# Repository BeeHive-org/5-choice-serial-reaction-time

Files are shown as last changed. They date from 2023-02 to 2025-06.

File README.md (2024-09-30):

# Serial Reaction Chamber

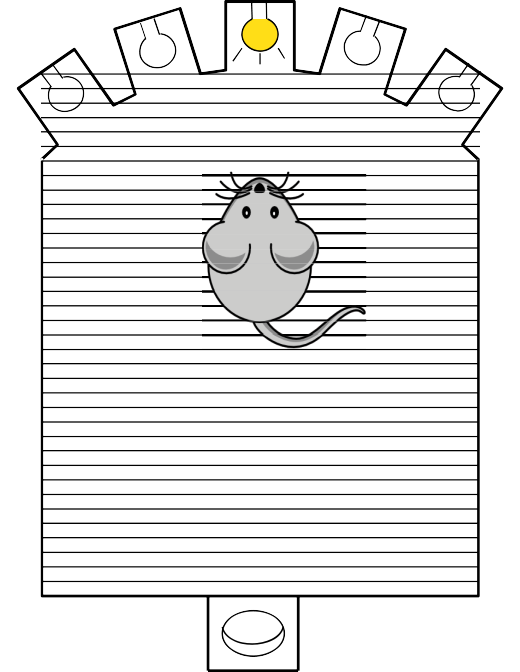
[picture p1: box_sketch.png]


The chamber can be used to observe small rodents response to light stimulus. 

It has holes with a light on one end and a feeding slot with a light in the opposite end. Depending on the behavoiur being experimented the animal needs to poke it's nose into the correct hole and feeding occurs in accordance to the experiemntal rules.

 Its an implementation of a complete behavioural box using BeeHive, off the shelf components and 3D printed parts.
  
---

### Hardware:
- The supporting hardware for the project:
     * food_dispencer
    * reaction_chamber 
- Running on the Beehive platform under:
     + Electronics 

### Software:
-    The beehive platform uses ESP32 which can run either micropython or C++. 
-     testcode is provided in microPython.
 -   You can also use Bonsai for data collection on PC however this implimentation is not covered under this documentation.

If you wish to build the complete box please look at the [Overal BOM]{BOM} otherwise you can find indvidual sectional Bill of materials under each tab.

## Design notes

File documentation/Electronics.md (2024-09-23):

# Electronics

The electronics combine the Esp32 and Bee hive central hub:

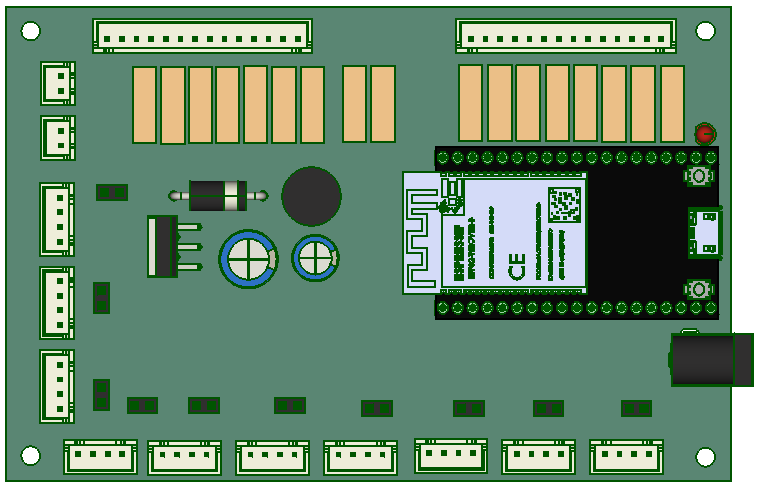
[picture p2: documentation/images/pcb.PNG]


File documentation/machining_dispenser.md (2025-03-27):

[3d printer]:Parts.yaml#3dprinter
[Laser cutter]:Parts.yaml#Lasercutter
[PLA filament]:Parts.yaml#PLAfilament
[clear plastic sheet]:Parts.yaml#ClearSheet

# Machining Guide

>! To accomplish this section you should have appropriate machining skills. 
>? You can outsource the parts by sending this section to your preffered machining techinician or company.

{{BOM}}

##Printing parts{pagestep}

>? Support from bed plate is required. It is unnecesary to add support everywhere. Add a brim to ensure the small parts are anchored appropriately. 

*  Use a [3d printer]{qty: 1, cat:machine} and [PLA filament]{ qty:100g, cat:material} to print the following parts:
       +  [Motor holder](models/Motor_holder.stl)
       +  [Tank base](models/Allparts.stl)
       +  [Chute](models/chute_with_mount.stl)
       +  [Feed tank](models/Feed_tank.stl)
       +  [Rotor](models/Rotor.stl)

## Laser cut parts {pagestep}

* Use a [Laser cutter]{qty: 1, cat:machine} and [clear plastic sheet]{qty:1, cat: material} to produce the following:
    + [Outer cover](models/Outer_cover.svg)
    + [Inner cover](models/Inner_cover.svg)

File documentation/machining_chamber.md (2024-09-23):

[3d printer]:Parts.yaml#3dprinter
[Laser cutter]:Parts.yaml#Lasercutter
[PLA filament]:Parts.yaml#PLAfilament
[clear plastic sheet]:Parts.yaml#ClearSheet
[maker beam XL]:Parts.yaml#MakerBeamXL
[150mm mini hacksaw]:Parts.yaml#Hacksaw
[M3 tap set]:Parts.yaml#M3tapset
[tap wrench]:Parts.yaml#Tapwrench

# Machining Guide

>! To accomplish this section you should have appropriate machining skills. 
>? You can outsource the parts by sending this section to your preffered machining techinician or company.

{{BOM}}

## Printing parts{pagestep}

>? Support from bed plate is required. It's unnecesary to add support everywhere. Add a brim to ensure the small parts are anchored appropriately. 

*  Use a [3d printer]{qty: 1, cat:machine} and [PLA filament]{ qty:500g, cat:material} to print the following parts:
    + [Latch handle](models/Latch_handle.stl)
    + [Latch base](models/Latch_base.stl)
    + [Electronics top](models/Electronics_top.stl)
    + [Corner](models/corner.stl)
    + [Feeding wall](models/Feeding_wall.stl)
    + [Led series wall](models/Led_series_wall.stl)
    + [Curved wall](models/Curved_wall.stl)
    + [Tunnel connector](models/Tunnel_connector.stl)
    + [Tunnel clamp](models/Tunnel_clamp.stl)
    +  [Hinge](models/Hinge.stl)
    + [Trap latch](models/Trap_latch.stl)
    + [Groove pins](models/Grooved_pin.stl)

## Laser cut parts{pagestep}
* Use a [Laser cutter]{qty: 1, cat:machine} and [clear plastic sheet]{qty:1, cat: material} to produce the following:
     + 1 pc of [Ecase_Back](models/Ecase_Back.svg)
     + 1 pc of [Ecase_Base](models/Ecase_Base.svg)
     + 1 pc of [Ecase_Front](models/Ecase_Front.svg)
     +  2 pcs of [Ecase_R&L](models/Ecase_RnL.svg)
     + 1 pc of [platform support](models/Platform_support.svg)
     + 2 pcs of [Platform base](models/Platform_base.svg)
     + 1 pc of [side entry wall](models/Side_entry_wall.svg)
     + 1 pc of [side plain wall](models/Side_plain_wall.svg)
     + 1 pc of [case back](models/Excrete_panel_RnL.svg),
     + 1 pc of [case base](models/Excrete_panel_base.svg)
     + 1 pc of [case front](models/Excrete_panel_RnL.svg) 
     + 1 pc of [case right](models/Excrete_panel_FnB.svg) 
     + 1 pc of [case left](models/Excrete_panel_FnB.svg) 

## Cut and thread beams{pagestep}
 + Using [150mm mini hacksaw]{Qty:1,cat: Tool} cut 2 pcs 200mm long and 6 pcs 150mm long from the [maker beam XL]{Qty:1,cat: material}
 
  + From the [M3 tap set]{Qty:1,cat: Tool} place the taping screw on the [tap wrench]{Qty:1,cat: Tool} then make threads on the holes at the end of the maker beam xl pieces.

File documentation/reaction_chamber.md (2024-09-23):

# Reaction chamber

The chamber is used to track mice reaction time using light as a training cue. Coupled with a camera it can be used to collect data on movement patterns, posture and other behaviours. 

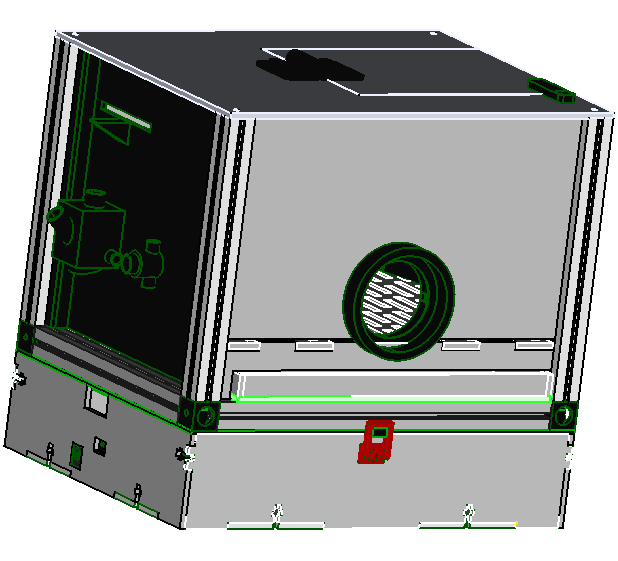
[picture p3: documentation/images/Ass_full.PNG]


Before you start ensure you have everything by checking the [bill of materials page]{BOM}.

You can then follow the guides below:

* [.](machining_chamber.md){step}
* [.](make_chamber.md){step}

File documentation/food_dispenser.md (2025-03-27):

# Food dispenser

An automated feeding and storage tank for small animals during lab test. In this project its being used to reward the animal under test. After testing is done the feeding tank should be filled and programed to auto feed mode to ensure the animal is feed as per the diatery requirements.

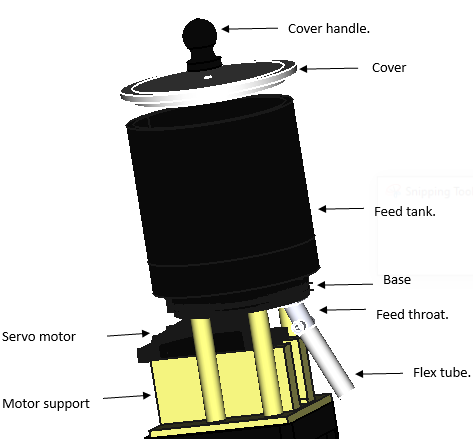
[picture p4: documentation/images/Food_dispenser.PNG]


Before you start ensure you have everything by checking the [bill of materials page]{BOM}.

You can then follow the guides below:

* [.](machining_dispenser.md){step}
* [.](make_dispenser.md){step}

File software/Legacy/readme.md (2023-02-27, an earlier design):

this folder contains the code to run the 5-CSRTT training and test.  
    
To setup the board to communicate over wifi and use Belay users need to:  
- Make a copy of the "passes_template.py" and rename it to passes.py  
- Change the newly created "passes.py" file to contain needed information about the network and where the IP address for Bonsai  
- Save "passes.py" on the ESP32 board  
- Save "webrepl_cfg.py" on the ESP32 board  
-  

More documentation on Belay connections here:  
https://belay.readthedocs.io/en/latest/Connections.html  

---  

phases of training and testing are:  
 -food_magazine  
 -phase1  
 -phase2  
 -stage_5csrtt_task  
 -stage_9_task  
 -stage_10_task  
 -stage_11_task  
 -stage_12_task

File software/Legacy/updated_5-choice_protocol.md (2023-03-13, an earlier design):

##### Updated 5-Choice Training Program

## New nosepoke light to trigger trial start at the back panel in the middle
## Magazine will be moved to right hand side

* TSL = Trial Start Light
* TSS = Trial Start Sensor
* MS = Magazine Sensor
* FD = food delivery

## Magazine Training:

* TSL turns on + food is delivered
* mouse nosepokes into the magazine to get the food
* this triggers TSL to turn off + variable ITI begins (4,8,16,or 32 sec)
* next trial begins
* This phase is 50 trials.

## Training 1 (Phase 1):

* TSL turns on 
* mouse nosepokes into Trial Start Hole + TSS detects it
* TSL turns off + food is delivered
* mouse nosepokes into the magazine to get the food
* next trial begins
* This phase is 50 trials.

## Training 2 (Phase 2):

* TSL turns on 
* mouse nosepokes into Trial Start Hole + TSS detects it
* TSL turns off
* 5 stimulus lights on the opposite wall turns on
* mouse nosepokes into one of them (sensor detects it)
* 5 stimulus lights turn off
* food is delivered
* next trial begins
* This phase is 50 trials.

## Training 3 (Phase 3):

* TSL turns on 
* mouse nosepokes into Trial Start Hole + TSS detects it
* TSL turns off
* 5 sec ITI
* Randomly chosen 1 stimulus light on the opposite wall turns on
* mouse nosepokes into one of them (sensor detects it)
* If nosepoked into a non-illumniated hole, there is no consequence, the trial begins again.
  * all lights off, no time out, start at the beg. again.
* If mouse nosepokes into the illuminated light, stimulus light turns off.
* food is delivered
* once mouse collects the food, there is 20 sec consumption interval (no light is on)
* next trial begins
* This phase is 100 trials.

## 5-Choice Training (Phase 4-8):

* TSL turns on 
* mouse nosepokes into Trial Start Hole + TSS detects it
* TSL turns off
* 5 sec ITI
* one Nosepoke turns on for SD time and turns off after that duration.
* If nosepoke into stimulus lights during ITI, record it as premature and Time-Out for 5 sec (no lights).
* Randomly chosen 1 stimulus light on the opposite wall turns on
* mouse nosepokes into one of them (sensor detects it)
* If nosepoked into a non-illumniated hole, record it as incorrect and Time-Out for 5 sec (no lights).
* If mouse nosepokes into the illuminated light, stimulus light turns off.
* food is delivered
* once mouse collects the food from magazine, there is 20 sec consumption interval (no light is on)
* If no nosepokes (SD+4sec), record it as an omission and Time-Out for 5 sec (no lights).
* next trial begins
* This phase is 100 trials.

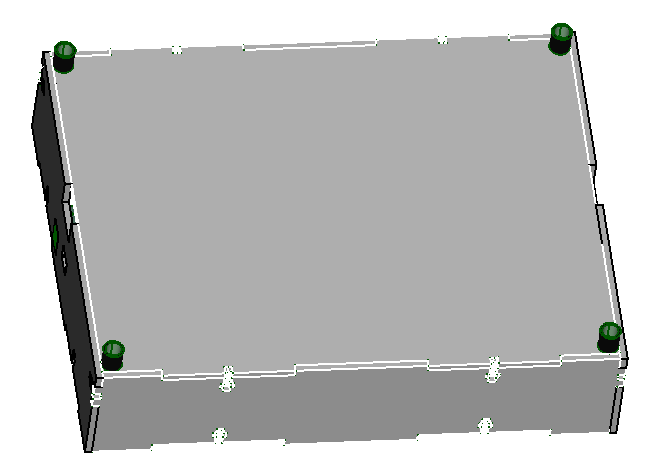
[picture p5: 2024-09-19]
documentation/images/Electronics_full.PNG

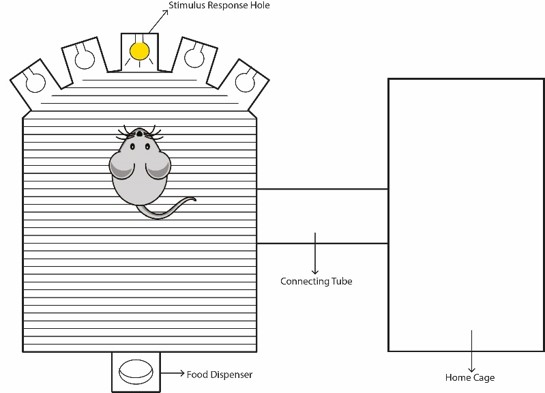
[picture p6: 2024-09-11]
documentation/images/CombiCage_sketch.jpg

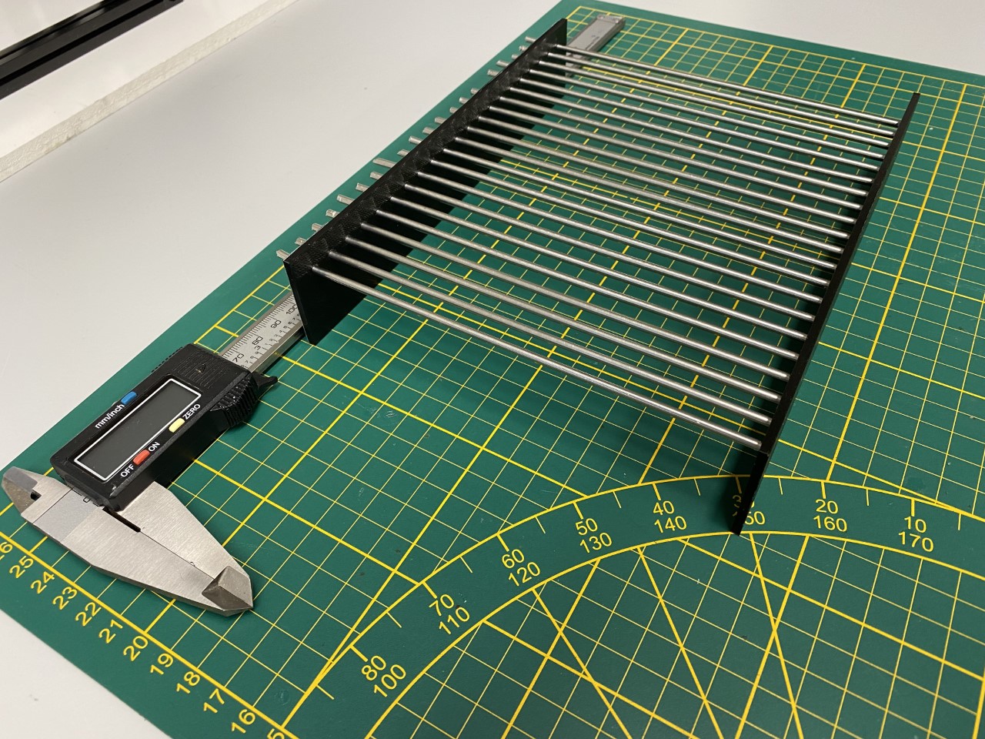
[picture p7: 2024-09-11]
documentation/images/grid_5.jpg

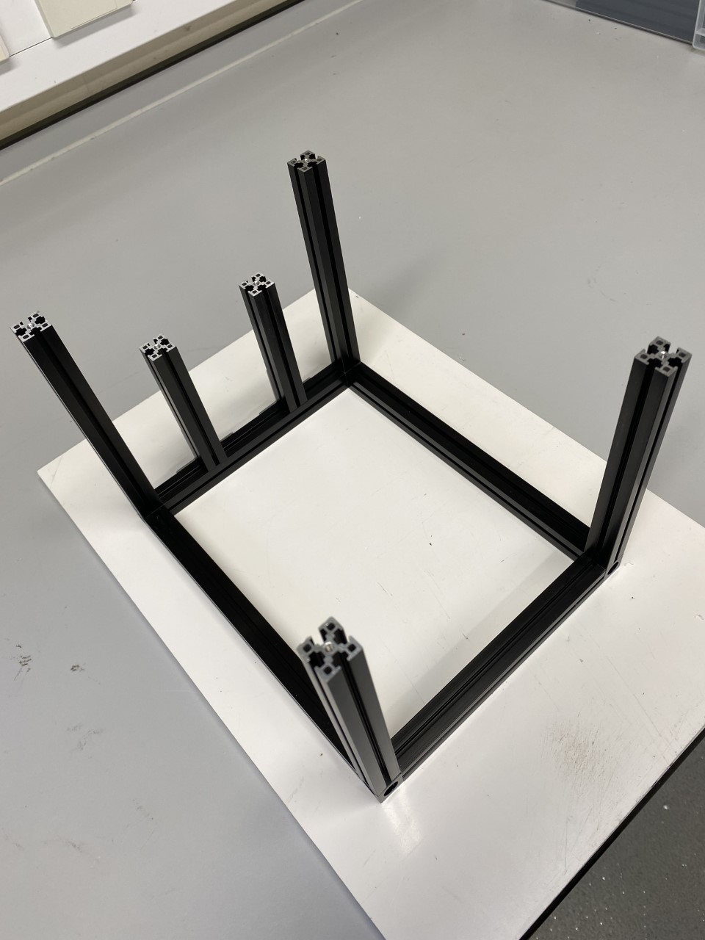
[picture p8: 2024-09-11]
documentation/images/frame_2.jpg

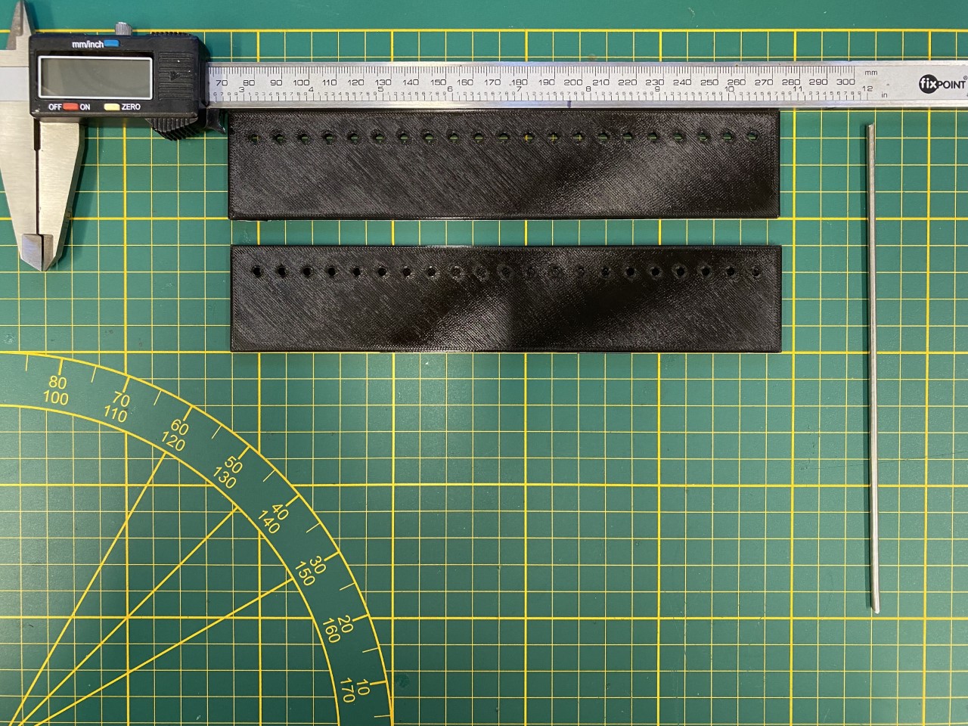
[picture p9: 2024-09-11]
documentation/images/grid_2.jpg

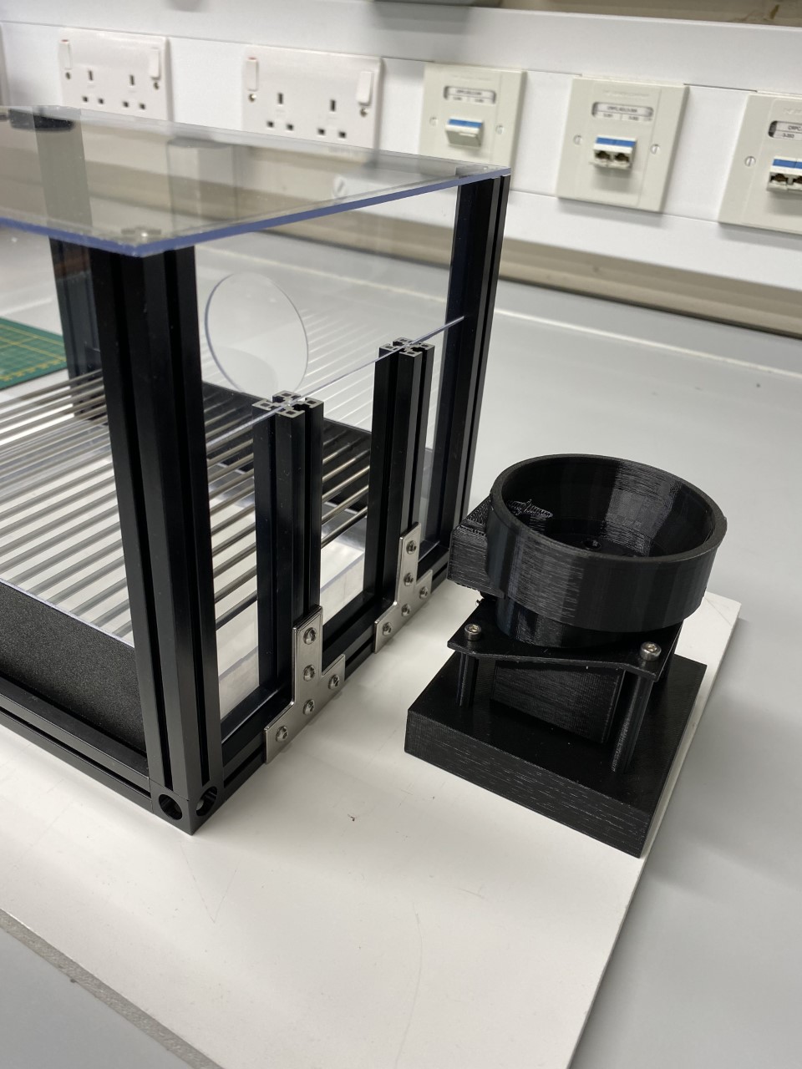
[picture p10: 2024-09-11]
documentation/images/box_2.jpg

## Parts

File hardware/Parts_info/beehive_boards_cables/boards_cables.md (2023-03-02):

##### Hardware: boards and cables

#### 5 boards:

### Main board: (Everything is connected to it)

* Connectors – 4 : 10 
* XH header – 4 : 10
* XH cables : 34

### Sensor board: (sensors for 4 NP and F.M)
 
## 5 Sensors and 5 IR lights
## 20 cables

* Connectors – 2 : 10 
* XH header – 2 : 10
* Connectors – 4 : 3
* XH header – 4 : 3
* XH cables: 32

### Sensors Board 2 (sensors for 1 NP and Food dispenser)

## 3 Sensors and 3 IR lights
## 12 cables

* Connectors – 2 : 6 
* XH header – 2 : 6
* Connectors – 4 : 2
* XH header – 4 : 2
* XH cables: 20

### Yellow LEDs board

## 6 yellow LEDs
## 12 cables

* Connectors – 2 : 6 
* XH header – 2 : 6
* Connectors – 4 : 3
* XH header – 4 : 3
* XH cables: 24

### Stepper Motor:

* Connectors – 2 : 1
* XH header – 2 : 1
* Connectors – 4 : 1
* XH header – 4 : 1
* XH cables: 6

* Connectors – 5 : 1
* XH header – 5 : 1

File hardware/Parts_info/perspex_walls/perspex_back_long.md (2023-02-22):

#### Perspex Back Wall Long Dimensions:

* Length = 16 cm
* Width = 5 cm
* Thickness = 2.5 mm

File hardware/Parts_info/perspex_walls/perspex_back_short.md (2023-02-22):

#### Perspex Back Wall Short Dimensions:

* Length = 10.1 cm
* Width = 4.3 cm
* Thickness = 2.5 mm

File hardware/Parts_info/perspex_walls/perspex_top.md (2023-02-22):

#### Perspex Top Dimensions:

* Length = 22.8cm
* Width = 18 cm
* Length from middle (curved on one side) = 23.9 cm
* Thickness = 2.5 mm

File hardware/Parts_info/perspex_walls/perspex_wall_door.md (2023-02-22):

#### Perspex Wall Door Dimensions:

* Length = 20.6 cm
* Width = 11 cm
* Thickness = 2.5 mm

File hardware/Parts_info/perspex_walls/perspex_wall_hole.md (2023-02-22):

#### Perspex Wall Door With Hole Dimensions:

* Length = 20.6 cm
* Width = 11 cm
* From the hole to corner = 7.8 cm
* From the hole to top = 5.6 cm
* Diameter of the hole = 5.3 cm
* Thickness = 2.5 mm

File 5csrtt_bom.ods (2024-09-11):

what | qty | unit price | total price | obs | where | grand total
XH headers 4 positions | 20 | 0.22 | 4.4 |  | https://www.digikey.co.uk/en/products/detail/jst-sales-america-inc/B4B-XH-A-LF-SN/1651047 | 317.24
XH cable housing 4 positions | 40 | 0.11 | 4.4 |  | https://www.digikey.co.uk/en/products/detail/jst-sales-america-inc/XHP-4/683353
XH cable crimpped | 60 | 0.86 | 51.6 |  | https://www.digikey.co.uk/en/products/detail/jst-sales-america-inc/ASXHSXH22K305/6684932
xh headers 2 positions | 30 | 0.17 | 5.1 |  | https://www.digikey.co.uk/en/products/detail/jst-sales-america-inc/B2B-XH-AM-LF-SN/1016630
XH cable housing 2 positions | 60 | 0.098 | 5.88 |  | https://www.digikey.co.uk/en/products/detail/jst-sales-america-inc/XHP-2/555485
28byj-48 stepper motor package of 5 with drivers | 1 | 17 | 17 |  | https://www.amazon.co.uk/GeeekPi-Stepper-28BYJ-48-Uln2003-Compatible/dp/B087BYKB6T
USB cable (micro) | 1 | 3.6 | 3.6 |  | https://www.digikey.co.uk/en/products/detail/assmann-wsw-components/AK67421-0-5/2263977
3D printing filament | 1 | 20 | 20 |  | https://www.digikey.co.uk/en/products/detail/esun/PLA-175J1/16733261
IR phototransistor | 12 | 0.6 | 7.2 |  | https://www.digikey.co.uk/en/products/detail/ams-osram-usa-inc/SFH-300/2205884
lm2596 | 1 | 5.7 | 5.7 |  | https://www.digikey.co.uk/en/products/detail/LM2596T-5.0-NOPB/LM2596T-5.0-NOPB-ND/363708
680uf capacitor | 1 | 0.4 | 0.4 |  | https://www.digikey.co.uk/en/products/detail/rubycon/16ZLH680MEFC10X12-5/3134108
33uh inductor | 1 | 1 | 1 |  | https://www.digikey.co.uk/en/products/detail/bourns-inc/6100-330K-RC/3782200
220 uf capacitor | 1 | 0.45 | 0.45 |  | https://www.digikey.co.uk/en/products/detail/rubycon/35ZLH220MEFCT78X11-5/3568150
Maker beam 200 mm | 2 | 2.6 | 5.2 |  | https://www.technobotsonline.com/makerbeamxl-200mm-long-black-anodised-beam-threaded.html
Makerbeam 150 mm | 6 | 2.2 | 13.2 |  | https://www.technobotsonline.com/makerbeamxl-150mm-long-black-anodised-beam-threaded.html
Makerbeam 100 mm | 2 | 1.7 | 3.4 |  | https://www.technobotsonline.com/makerbeamxl-100mm-long-black-anodised-beam-threaded.html
bolt M3, 6mm, A2 (package with 100) | 1 | 6 | 6 |  | https://www.technobotsonline.com/button-head-socket-cap-stainless-screw-m3x6mm-pk-100.html
M3 nut, A2 (package with 250) | 1 | 7 | 7
corner cubes (1 package with 12) | 1 | 19 | 19 |  | https://www.technobotsonline.com/makerbeam-corner-cube-kit-in-black-pack-of-12-with-hex-key.html
PCBs | 3 | 15 | 45 |  | JLCPCB
ESP32 | 1 | 10 | 10 |  | https://www.amazon.co.uk/dp/B071P98VTG?th=1
LED 8mm yellow | 6 | 0.35 | 2.1 |  | https://uk.rs-online.com/web/p/leds/2471814?gb=s
2.54 connectors | 2 | 2.35 | 4.7 |  | https://uk.rs-online.com/web/p/pcb-sockets/6816820?gb=s
IR led 5 mm | 12 | 0.95 | 11.4 |  | https://uk.rs-online.com/web/p/photodiodes/6548902?gb=a
acrylic sheet 250X250X3mm | 3 | 4.5 | 13.5 |  | https://www.directplastics.co.uk/acrylic-sheet
resistors 1kohm | 4 | 0.09 | 0.36 |  | https://www.digikey.co.uk/en/products/detail/te-connectivity-passive-product/CFR16J1K0/3317907
resistors 47 ohm | 4 | 0.4 | 1.6 |  | https://www.digikey.co.uk/en/products/detail/te-connectivity-passive-product/ROX1SJ47R/2381469
barrel jack | 1 | 1 | 1 |  | https://www.digikey.co.uk/en/products/detail/tensility-international-corp/54-00133/9685442
wire pair (20 m) | 1 | 11 | 11 |  | https://www.amazon.co.uk/C-able-Electric-Automotive-Extension-Electrical/dp/B07DHQK4JY
power supply | 1 | 12 | 12 |  | https://www.digikey.co.uk/en/products/detail/tri-mag-llc/ICM36-120/10445567
power supply plug | 1 | 1.4 | 1.4 |  | https://www.digikey.co.uk/en/products/detail/tri-mag-llc/888991000/10445553
Diode schottky | 1 | 0.65 | 0.65 |  | https://www.digikey.co.uk/en/products/detail/diodes-incorporated/SB5100-T/278636
Servo motor -MG996R | 1 | 9 | 9 |  | https://www.amazon.co.uk/AZDelivery-MG996R-Digital-Servo-Parent/dp/B082MN573T
Arcrylic | 1 | 13 | 13 |  | https://www.amazon.co.uk/Pack-Clear-Acrylic-Sheets-Transparent/dp/B0BXLQBD38?s=industrial
14 postion Jst connector(female) | 2 |  | 0 |  | https://uk.rs-online.com/web/p/pcb-headers/1755493?gb=s
14 postion Jst connector(male) | 2 |  | 0

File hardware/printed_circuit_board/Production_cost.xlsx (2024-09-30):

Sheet: Materials cost
Column1 | Column2 | Column3 | Column4 | Column5 | Column6 | Column7 | Column8
Name in documentation | Category | Qty | Price by packaging | Actual consumption | Supplier 1 | Part No | Link
3d printer | machine | 1 |  | £0.000 | RS | ENDER-3 S1 PRO | https://uk.rs-online.com/web/p/3d-printers/2857472?gb=s
Laser cutter | machine | 1 |  | £0.000 | RS | ENDER-3 S1 PRO | https://uk.rs-online.com/web/p/3d-printers/2857472?gb=s
clear plastic sheet | material | 1 | £65.000 | £65.000 | RS | 334-6472 | https://uk.rs-online.com/web/p/plastic-sheets/3346472?gb=s
Flexible Tube | material | 1 | £97.000 | £0.776 | RS | 260-4412 | https://uk.rs-online.com/web/p/hose-pipe-flexible-tubes/2604412?gb=s
maker beam XL | material | 1 | £11.270 | £11.270 | technobotsonline | 4447-087 | https://www.technobotsonline.com/makerbeamxl-1000mm-long-black-anodised-beam-threaded.html
PLA filament | material | 600 g | £37.160 | £37.160 | RS | 832-0214 | https://uk.rs-online.com/web/p/3d-printing-materials/8320214?gb=s
Liquid Adhesive | part | 1 | £8.540 | £8.540 | RS | 132-605 | https://uk.rs-online.com/web/p/adhesives/0132605?gb=a
M3 hex Nut | part | 14 | £4.630 | £4.630 | RS | 441-9098 | https://uk.rs-online.com/web/p/hex-nuts/4419098?gb=s
M3x8 Pozi pan machine screw | part | 38 | £3.820 | £1.719 | RS | 560-603 | https://uk.rs-online.com/web/p/machine-screws/0560603?gb=s
M3x8mm hex socket counter sunk screw | part | 8 | £7.430 | £1.486 | RS | 304-4918 | https://uk.rs-online.com/web/p/socket-screws/3044918?gb=s
Servo motor | part | 1 | £17.220 | £17.220 | RS | 781-3058 | https://uk.rs-online.com/web/p/servo-motors/7813058?gb=a
150mm mini hacksaw | tool | 1 | £13.990 | £0.000 | RS | 281-9162 | https://uk.rs-online.com/web/p/hand-saws/2819162?gb=a
2mm Hex key | tool | 1 | £5.530 | £0.000 | RS | 707-3282 | https://uk.rs-online.com/web/p/hex-keys/7073282?gb=s
M3 tap set | tool | 1 | £20.220 | £0.000 | RS | 215-552 | https://uk.rs-online.com/web/p/threading-taps/0215552?gb=s
Pozidriv PZ1 screw driver | tool | 1 | £5.620 | £0.000 | RS | 544-702 | https://uk.rs-online.com/web/p/screwdrivers/0544702?gb=a
tap wrench | tool | 1 | £11.660 | £0.000 | RS | 230-0112 | https://uk.rs-online.com/web/p/tap-die-wrenches/2300112?gb=a
Line Total |  |  | £309.090 | £147.801
Electronics
Name in documentation | Category | Qty | Unit price | Total | Supplier 1 | Part No | Link
ESP32-DEVKITC-32E | part | 1 | £7.670 | £7.670 | Digikey | 1965-ESP32-DEVKITC-32E-ND | https://www.digikey.co.uk/en/products/detail/espressif-systems/ESP32-DEVKITC-32E/12091810
Barrel jack | part | 1 | £0.636 | £0.636 | Digikey | CP-002AH-ND | https://www.digikey.co.uk/en/products/detail/same-sky-formerly-cui-devices/PJ-002AH/408446
Header pins | part | 1 | £1.740 | £1.740 | Digikey | 315-HDR200MET40F-G-V-TH-ND | https://www.digikey.co.uk/en/products/detail/chip-quik-inc/HDR200MET40F-G-V-TH/18869954
14 pin connector header | part | 2 | £0.924 | £1.848 | Digikey | A101096-ND | https://www.digikey.co.uk/en/products/detail/te-connectivity-amp-connectors/1-2132230-4/2288196
15 pin connector plug | part | 2 | £0.288 | £0.576 | Digikey | A117175-ND | https://www.digikey.co.uk/en/products/detail/te-connectivity-amp-connectors/1-1969442-4/4731001
crimp pins | part | 28 | £0.096 | £2.688 | Digikey | A101122CT-ND | https://www.digikey.co.uk/en/products/detail/te-connectivity-amp-connectors/2110989-1/2288222
Jst connector header | part | 6 | £0.216 | £1.296 | Digikey | 455-B4B-XH-A-ND | https://www.digikey.co.uk/en/products/detail/jst-sales-america-inc/B4B-XH-A/1651047
Jst connector plug | part | 6 | £0.096 | £0.576 | Digikey | 455-2267-ND | https://www.digikey.co.uk/en/products/detail/jst-sales-america-inc/XHP-4/683353
Crimp pins | part | 24 | £0.096 | £2.304 | Digikey | 455-2261-2-ND | https://www.digikey.co.uk/en/products/detail/jst-sales-america-inc/SXH-002T-P0-6/1651063
10k ohms resistor | part | 7 | £0.096 | £0.672 | Digikey | RNF14FTD10K0TR-ND | https://www.digikey.co.uk/en/products/detail/stackpole-electronics-inc/RNF14FTD10K0/1706596
560 ohms resistor | part | 1 | £0.096 | £0.096 | Digikey | MFR-25FBF52-560R-ND | https://www.digikey.co.uk/en/products/detail/yageo/MFR-25FBF52-560R/9138191
1k ohms resistor | part | 1 | £0.096 | £0.096 | Digikey | CF14JT1K00TR-ND | https://www.digikey.co.uk/en/products/detail/stackpole-electronics-inc/CF14JT1K00/1741314
47 ohms resistor | part | 7 | £0.096 | £0.672 | Digikey | 13-MFR-25FRF52-47RTR-ND | https://www.digikey.co.uk/en/products/detail/yageo/MFR-25FRF52-47R/9139055
33Uh inductor | part | 1 | £0.260 | £0.260 | Digikey | RLH0912-331KL-ND | https://www.digikey.co.uk/en/products/detail/bourns-inc/RLH0912-331KL/4700529
Diode | part | 1 | £0.528 | £0.528 | Digikey | 3757-SB520_R2_00001TR-ND | https://www.digikey.co.uk/en/products/detail/panjit-international-inc/SB520-R2-00001/15796470
680 uf capacitor | part | 1 | £0.492 | £0.492 | Digikey | 1189-1150-ND | https://www.digikey.co.uk/en/products/detail/rubycon/16ZLH680MEFC10X12-5/3134108
220uf capacitor | part | 1 | £0.168 | £0.168 | Digikey | 1189-1726-ND | https://www.digikey.co.uk/en/products/detail/rubycon/16ZLH220MEFC6-3X11/3563156
Voltage regulator | part | 1 | £5.424 | £5.424 | Digikey | LM2596T-5.0/NOPB-ND | https://www.digikey.co.uk/en/products/detail/texas-instruments/LM2596T-5-0-NOPB/363708
22 AWG wire | part | 1 | 0.27 | £0.270 | Digikey | CN190BR-500-ND | https://www.digikey.co.uk/en/products/detail/cnc-tech/21458-22-2-0500-0104-1-TS/5210508
PCBs | part | 1 | £15.00 | £15.00 | JLCPCB |  | JLCPCB
Shrink tube | part | 100 | 0.0449 | £4.490 | Digikey | SFTW2116K-1000-ND | https://www.digikey.co.uk/en/products/detail/3m/SFTW203-1-16-BL-SPL/269589
8mm Yellow led | part | 7 | 0.408 | £2.856 | Digikey | WP793YD-ND | https://www.digikey.co.uk/en/products/detail/kingbright/WP793YD/3084261
5mm Infrared emiiter | part | 7 | 0.708 | £4.956 | Digikey | 365-1058-ND | https://www.digikey.co.uk/en/products/detail/tt-electronics-optek-technology/OP293A/498684
2mm Infrared emiiter | part | 1 | 0.768 | £0.768 | RS | TSAL4400 | https://uk.rs-online.com/web/p/ir-leds/6997629?searchId=8170d003-decd-4315-aeb6-cb27a1b2b1c8&gb=s
5mm Phototransistor | part | 7 | 0.576 | £4.032 | Digikey | 1080-1019-ND | https://www.digikey.co.uk/en/products/detail/everlight-electronics-co-ltd/ALS-PT204-6C-L177/2675510
2mm Phototransistor | part | 1 | 0.338 | £0.338 | RS | TEFT4300 | https://uk.rs-online.com/web/p/phototransistors/7082731?searchId=eb0a8074-c099-4135-8f0a-0cff3d53b3ef&gb=s
power supply | part | £1.000 | £12.000 | £12.000 | Digikey |  | https://www.digikey.co.uk/en/products/detail/tri-mag-llc/ICM36-120/10445567
power supply plug | part | £1.000 | £1.400 | £1.400 | Digikey |  | https://www.digikey.co.uk/en/products/detail/tri-mag-llc/888991000/10445553
Line Total |  |  |  | £73.852
Grand Total |  |  |  | £221.653

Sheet: Production cost
Activity | time (hour) | cost | Total
Prinitng | 6 | £15.00 | £90.00
Laser cutting | 2.5 | £20.00 | £50.00
labour | 5 | £30.00 | £150.00
Total |  |  | £290.00

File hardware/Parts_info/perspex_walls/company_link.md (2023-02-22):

#### Link of the company:

https://www.directplastics.co.uk/

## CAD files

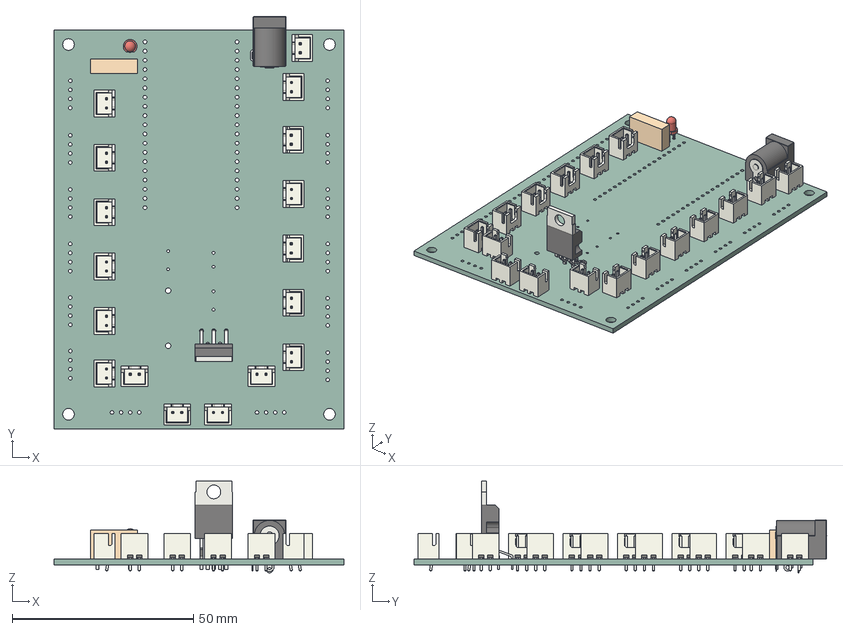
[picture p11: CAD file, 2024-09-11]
hardware/printed_circuit_board/main_pcb/main_pcb.step
80.0 x 113.8 x 25.3 mm
JST_B2B_XH_A x 17
BarrelJack_Horizontal
LED_D3.0mm
R_Box_L130mm_W40mm_P900mm
TO_220_5_Pentawatt_Multiwatt_5_Vertical_StaggeredType1
main_pcb_PCB

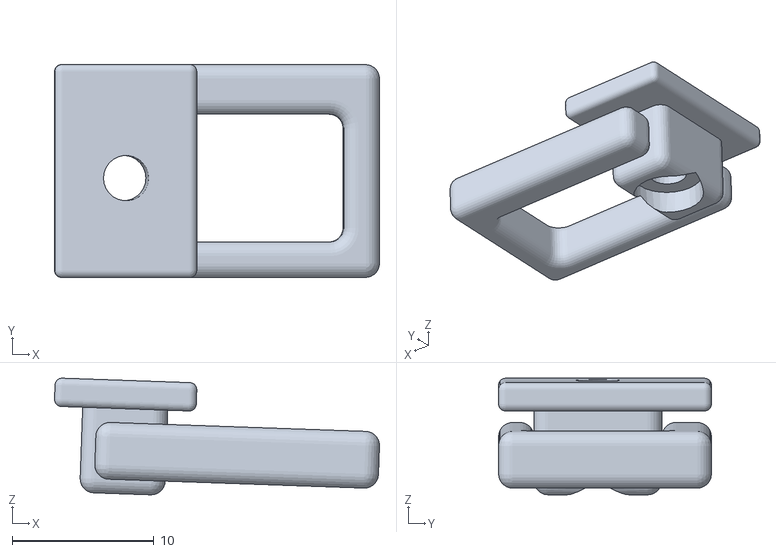
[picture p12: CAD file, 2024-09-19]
hardware/models/Latch_assembly.stl
22.9 x 15.0 x 8.22

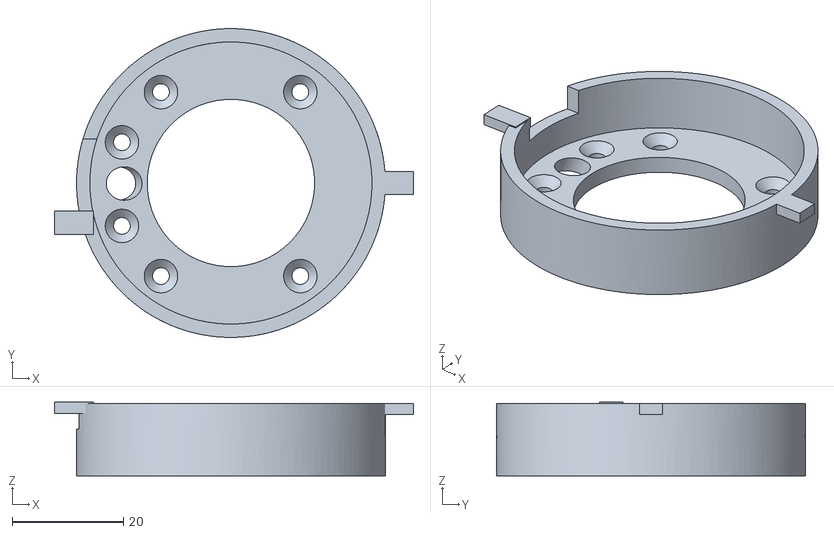
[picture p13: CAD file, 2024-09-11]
documentation/models/base.stl
64.4 x 55.4 x 13.2

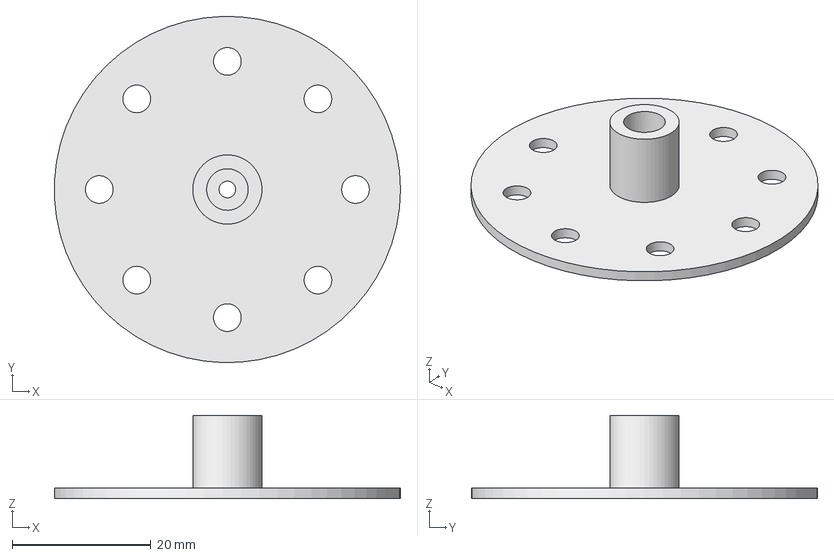
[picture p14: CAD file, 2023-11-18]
hardware/3Dparts/food_dispenser/rotor.FCStd
50.0 x 50.0 x 12.0 mm

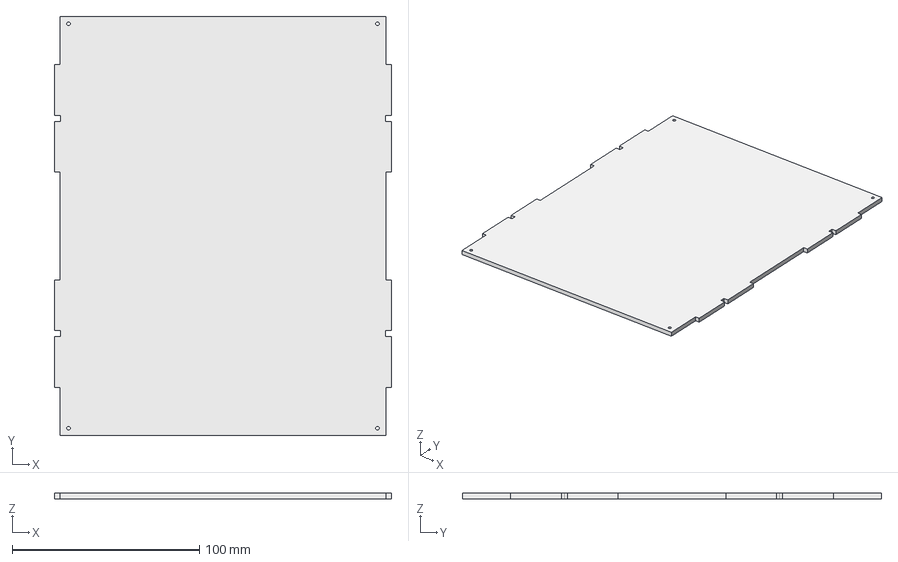
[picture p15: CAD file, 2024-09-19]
hardware/3Dparts/Reaction_chamber/Ecase_Top.step
180.0 x 224.0 x 3.00 mm

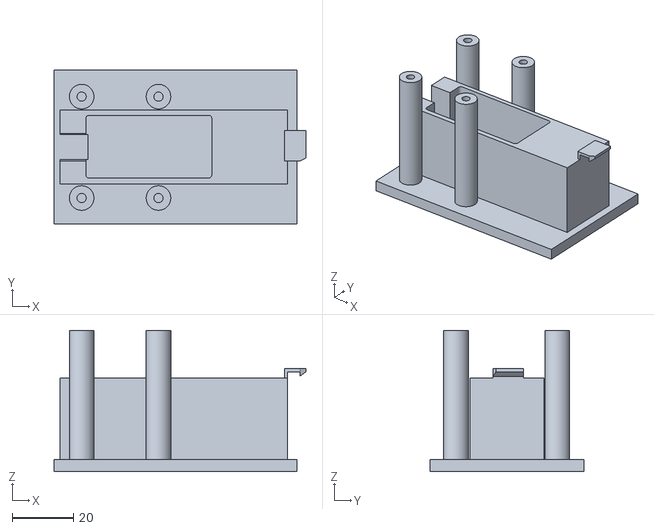
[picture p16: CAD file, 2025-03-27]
hardware/models/Motor_holder_modified.stl
82.0 x 50.0 x 46.0

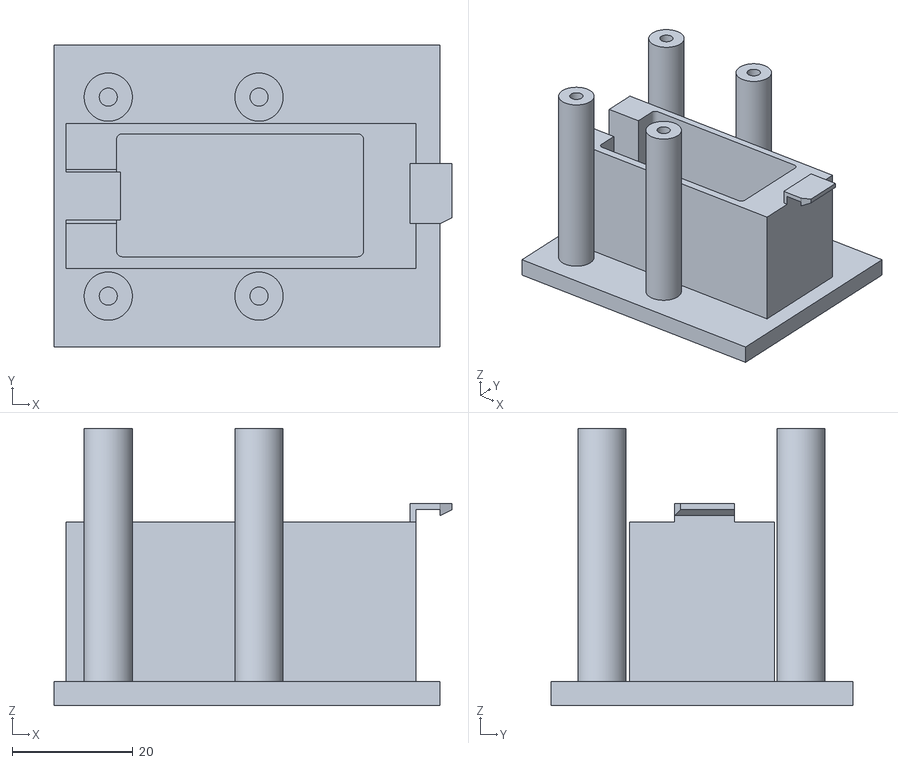
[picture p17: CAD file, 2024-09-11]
documentation/models/Motor_holder.stl
66.0 x 50.0 x 46.0

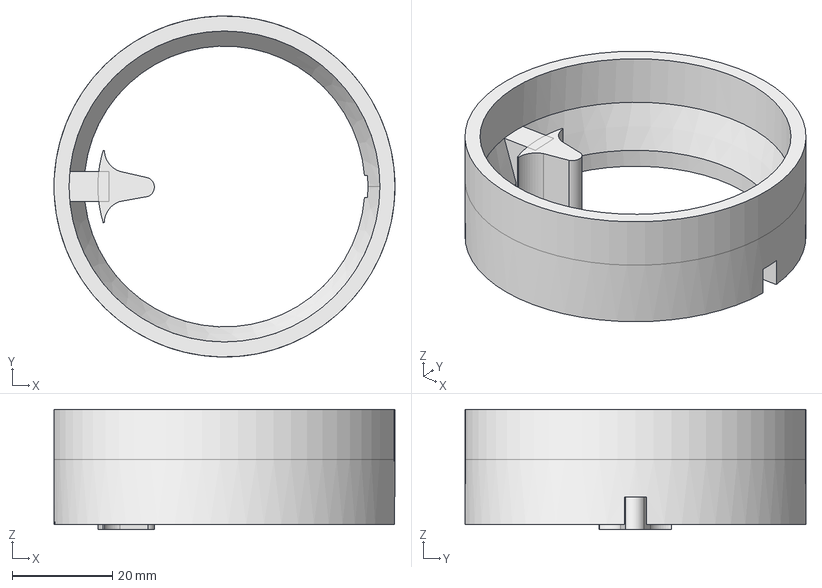
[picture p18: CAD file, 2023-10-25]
hardware/3Dparts/food_dispenser/lid.FCStd
68.0 x 68.0 x 24.0 mm

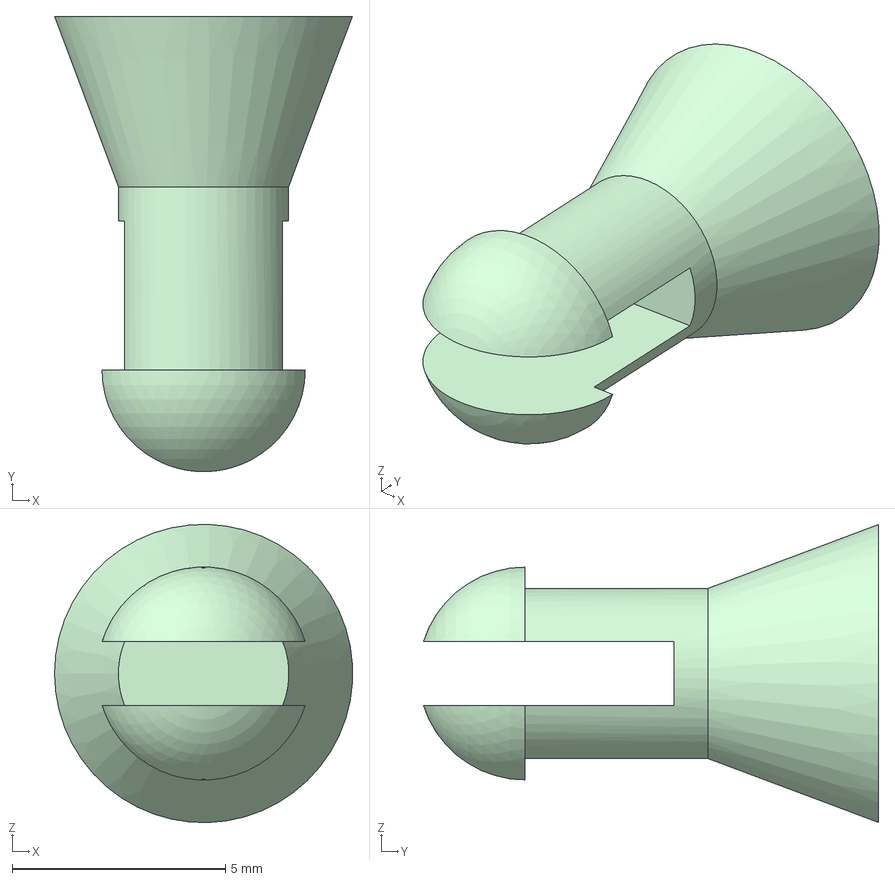
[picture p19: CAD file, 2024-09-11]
hardware/3Dparts/Reaction_chamber/Hinge_pin.step
6.99 x 10.7 x 7.00 mm

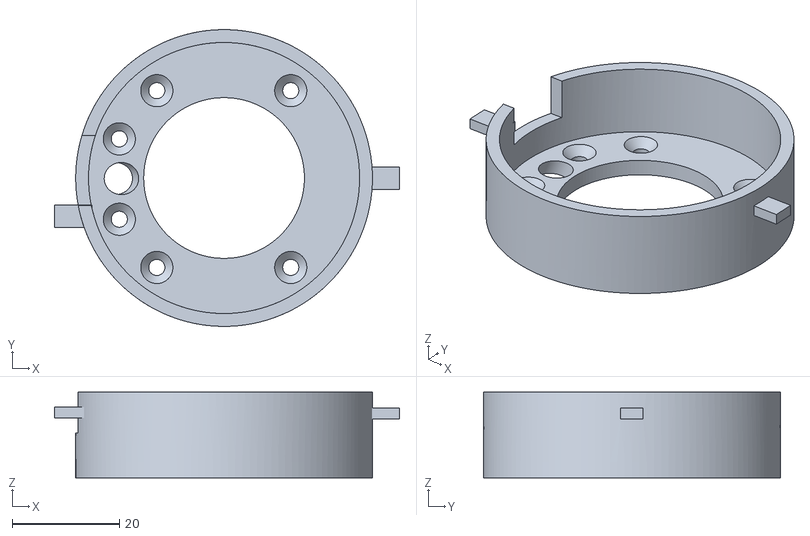
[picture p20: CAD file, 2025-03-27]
hardware/models/Base_modified.stl
64.4 x 55.4 x 16.0

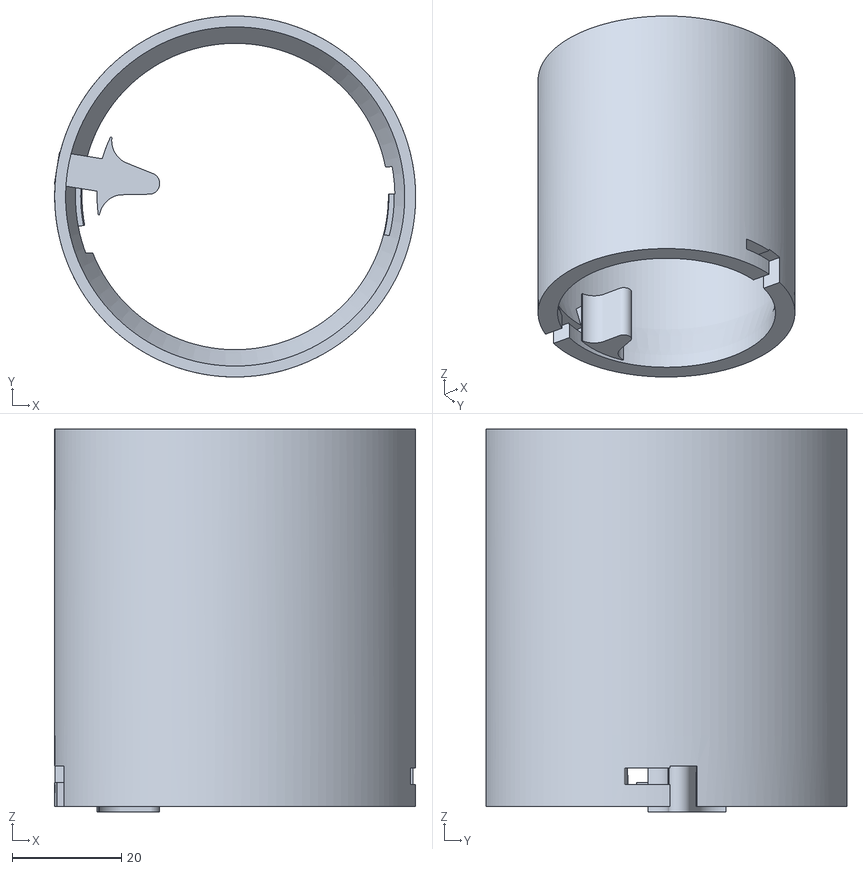
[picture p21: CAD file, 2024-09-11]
documentation/models/Feed_tank.stl
66.1 x 66.0 x 70.0

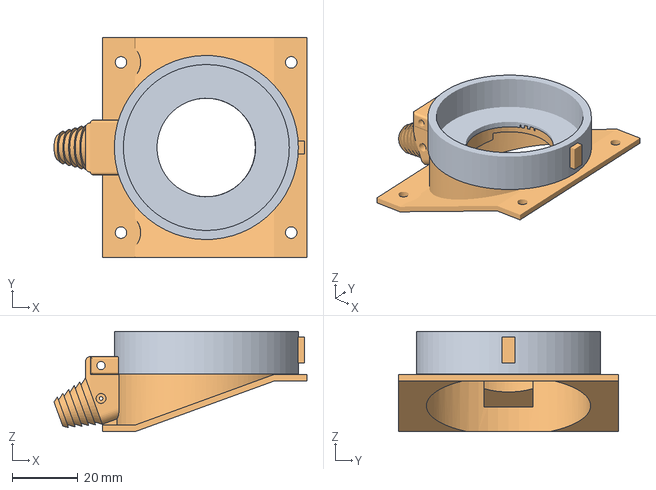
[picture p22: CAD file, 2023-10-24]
hardware/3Dparts/food_dispenser/food_dispenser_base.FCStd
77.0 x 66.8 x 30.5 mm
Base V7

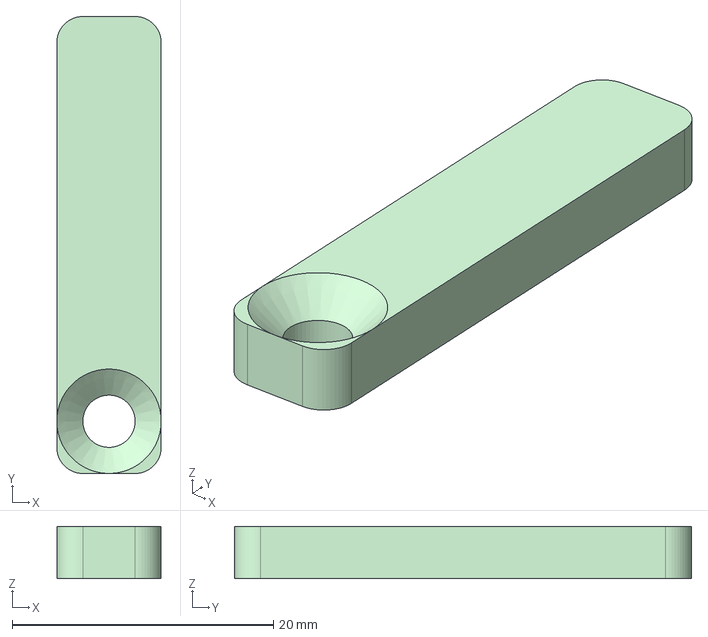
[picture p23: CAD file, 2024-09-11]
hardware/3Dparts/Reaction_chamber/latch.step
8.00 x 35.0 x 4.00 mm

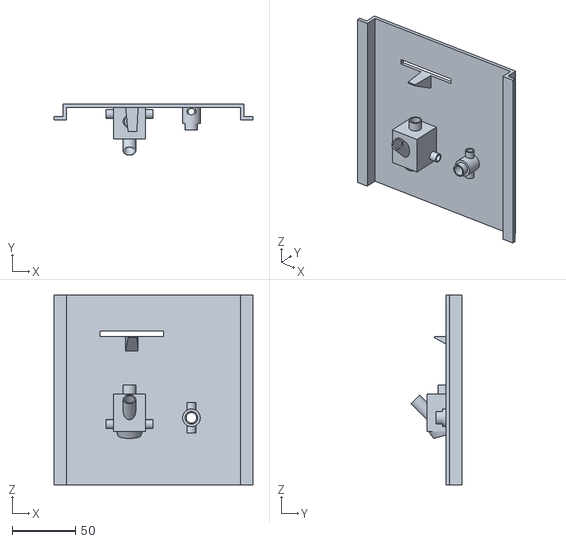
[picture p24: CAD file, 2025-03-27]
hardware/models/Feeding_wall.stl
157.4 x 40.7 x 150.0

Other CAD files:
documentation/models/Rotor.stl
hardware/models/Curved_wall.stl
hardware/models/Trap_latch.stl
hardware/models/Electronics_top.stl
hardware/3Dparts/Archive/backpanel.scad
hardware/3Dparts/Archive/base_in_case_needed.scad
hardware/3Dparts/Archive/curved_wall2.scad
hardware/3Dparts/Archive/gate.scad
hardware/3Dparts/Archive/Reaction_chamber.FCStd
hardware/3Dparts/Archive/bottom_grid_support.stl
hardware/3Dparts/Archive/connection_to_home_cage.stl
hardware/3Dparts/Archive/food_magazine.stl
hardware/3Dparts/Archive/grid.scad
hardware/3Dparts/Archive/grid_with_support.scad
hardware/3Dparts/Archive/magazine.scad
hardware/3Dparts/Archive/nose_poke.scad
hardware/3Dparts/Archive/nose_poke_parts.stl
hardware/3Dparts/Archive/nosepoke_back.scad
hardware/3Dparts/Archive/ring.scad
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

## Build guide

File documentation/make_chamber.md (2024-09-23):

[3d printer]:Parts.yaml#3dprinter
[Laser cutter]:Parts.yaml#Lasercutter
[PLA filament]:Parts.yaml#PLAfilament
[clear plastic sheet]:Parts.yaml#ClearSheet
[maker beam XL]:Parts.yaml#MakerBeamXL
[150mm mini hacksaw]:Parts.yaml#Hacksaw
[M3 tap set]:Parts.yaml#M3tapset
[tap wrench]:Parts.yaml#Tapwrench
[2mm Hex key]:Parts.yaml#2mmHexkey
[Pozidriv PZ1 screw driver]:Parts.yaml#PozidrivPZ1
[M3x8 Pozi pan machine screw]:Parts.yaml#M3X12mmPozipanscrews
[M3 hex Nut]:Parts.yaml#M3hexnut
[Liquid Adhesive]:Parts.yaml#Adhesive

# Assembly guide

{{BOM}}

## Electronics box{pagestep}

   + Assemble the Electronics box with the laser cut parts (Ecase_back,Ecase_front,Ecase_base,Ecase_RnL) to form a box then fasten the box with [M3 hex Nut]{Qty:12} and  [M3x8 Pozi pan machine screw]{Qty:12} using [Pozidriv PZ1 screw driver]{qty:1,cat:tool} to tighten the screws.

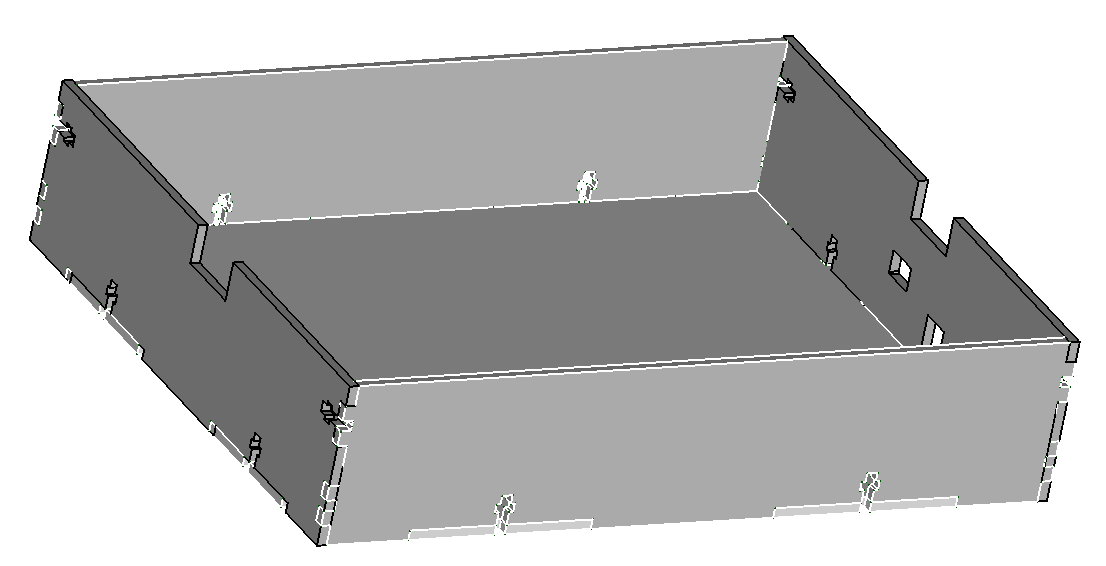
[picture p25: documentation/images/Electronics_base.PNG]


## Electronics board{pagestep}

   + Position the Pcb board in line with the holes on the side of the box assembly. Then using  [M3x8 Pozi pan machine screw]{Qty:4}fasten the board using  [Pozidriv PZ1 screw driver]{qty:1,cat:tool} to tighten the screws.

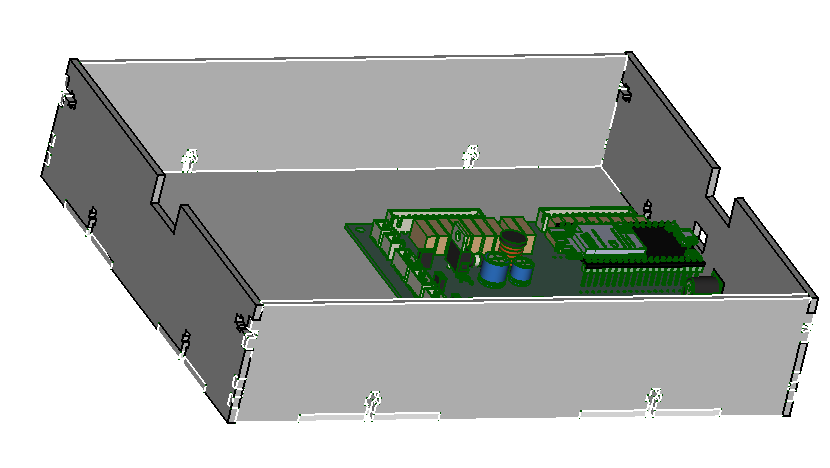
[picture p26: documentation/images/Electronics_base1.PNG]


## Electronics cover{pagestep}

>! Do not print the latch_assembly as one part 

   + Snap fit the [latch handle](models/Latch_handle.stl){previewpage} on to the [latch base](models/Latch_base.stl){previewpage}  part to from the [Latch_assembly](models/Latch_assembly.stl){previewpage}.

 + Locate the holes on the side of the box and using [M3 hex Nut]{Qty:2} and [M3x8 Pozi pan machine screw]{Qty:2} fasten the assembled latch to the box uisng [Pozidriv PZ1 screw driver]{qty:1,cat:tool}.   

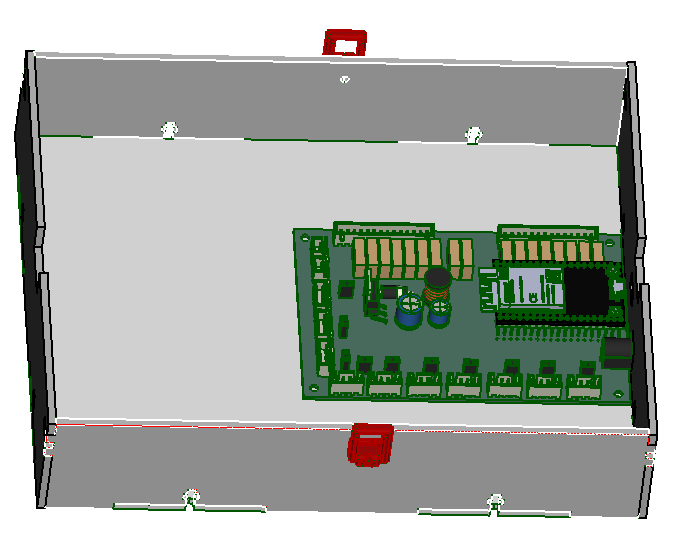
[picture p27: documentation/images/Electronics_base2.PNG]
   

 + Place the [Electronics top](models/Electronics_top.stl){previewpage} on top of the box and fasten it using the latch assembly.

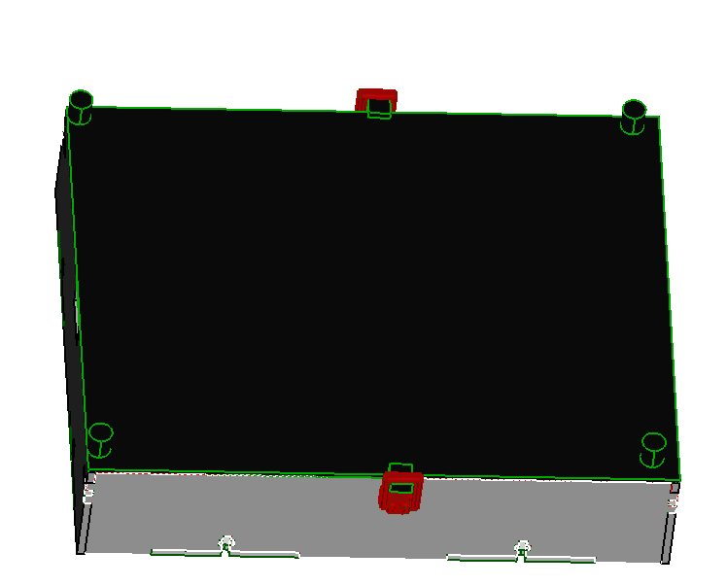
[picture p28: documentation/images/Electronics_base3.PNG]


## Maker beam frame{pagestep}

  + Place 2 makerbeam xl 200mm and 150 mm end to end at their meeting point joing them together using [corner](models/corner.stl){previewpage}. to make a square frame. Using [M3x8 Pozi pan machine screw]{Qty:12} fasten the corners to the maker beam xl uisng [Pozidriv PZ1 screw driver]{qty:1,cat:tool}. Repeat the process for all the corners to make a rectangle.

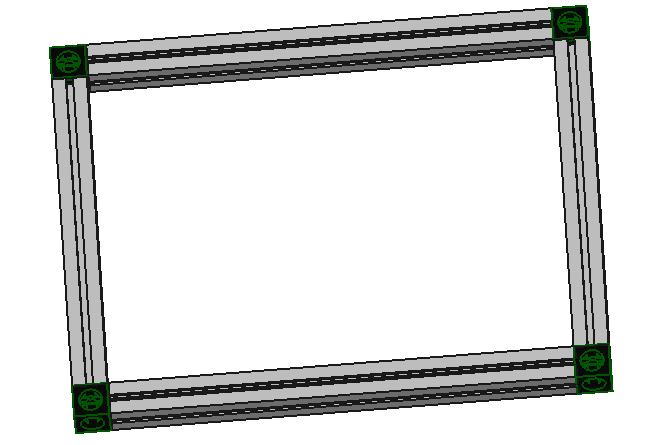
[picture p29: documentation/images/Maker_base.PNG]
  

  + At the corners of the square frame fasten horizontally 4 more maker beam xl using [M3x8 Pozi pan machine screw]{Qty:4}.  

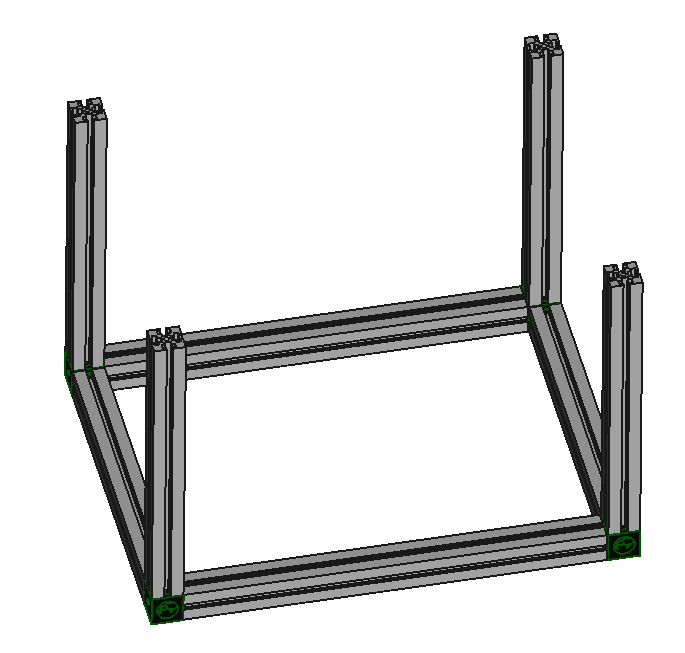
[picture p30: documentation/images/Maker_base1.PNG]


## Adding the enclosure{pagestep}

 + Slide the [platform support](models/Platform_support.svg) parts on opposite sides of the pillars and on top of them place the [Platform base](models/Platform_base.svg).

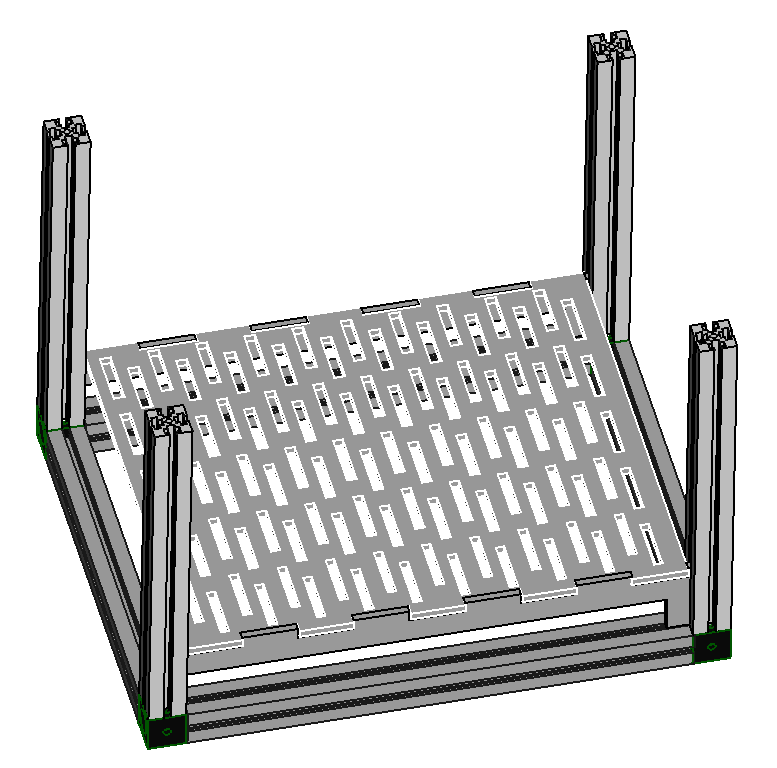
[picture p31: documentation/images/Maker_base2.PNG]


 + Slide the [feeding wall](models/Feeding_wall.stl){previewpage} making sure it goes all the way to the bottom. Then for the [led series wall](models/Led_series_wall.stl){previewpage} will slide up to the platform and on top of it slide the [curved wall](models/Curved_wall.stl){previewpage}.
.
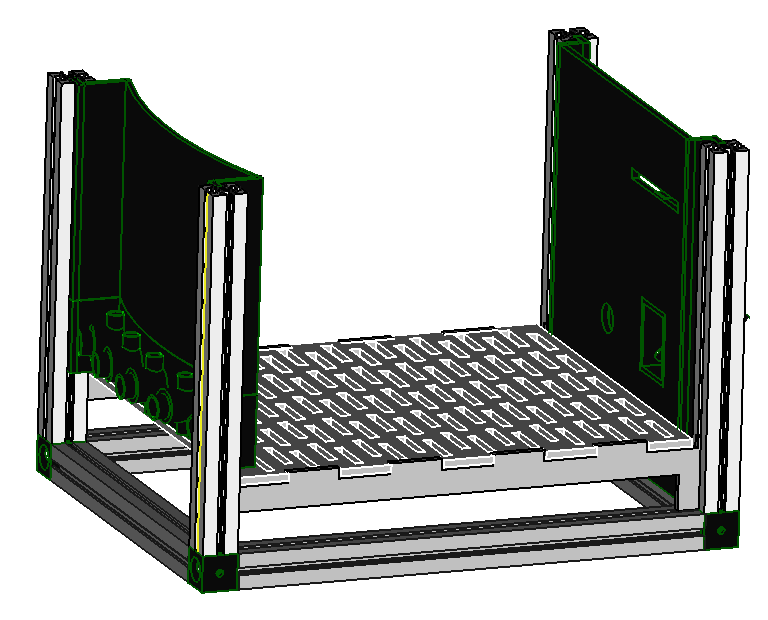
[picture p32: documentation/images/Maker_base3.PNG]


+ With the [side entry wall](models/Side_entry_wall.svg) press fit the [tunnel connector](models/Tunnel_connector.stl){previewpage} and the [tunnel clamp](models/Tunnel_clamp.stl){previewpage} on either side of the plasric sheet.

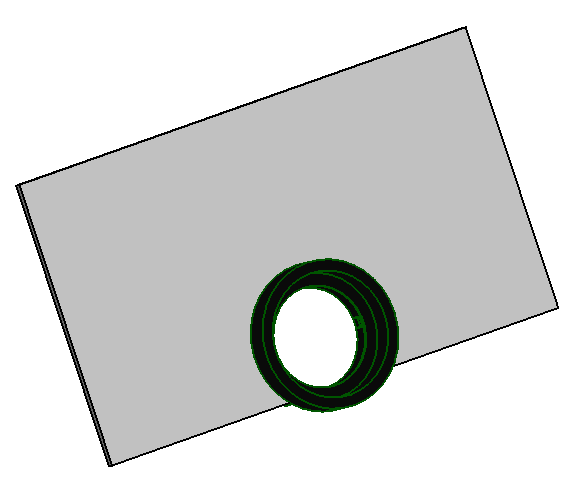
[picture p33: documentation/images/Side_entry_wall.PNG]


+ Slide the [side entry wall](models/Side_entry_wall.svg) and the [side plain wall](models/Side_plain_wall.svg) through the pillars of the box.

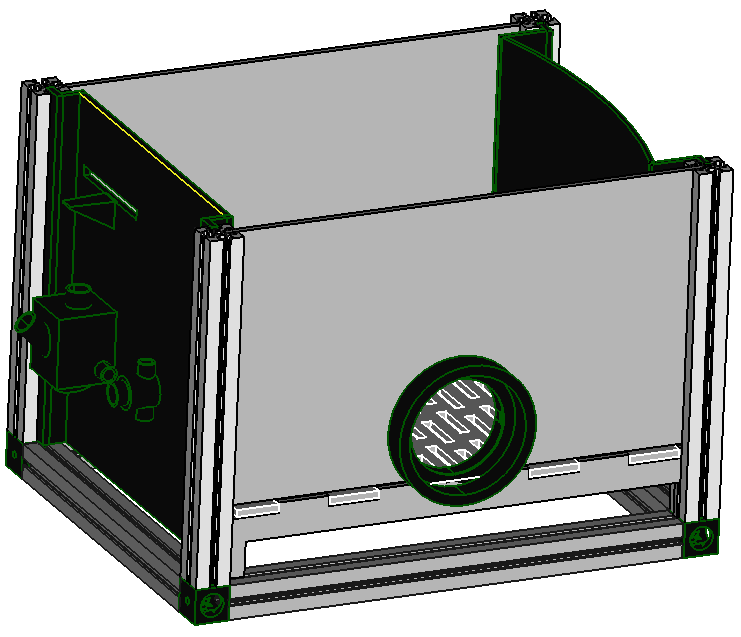
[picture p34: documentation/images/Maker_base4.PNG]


+ With the [lid](models/Lid.svg) pieces, [hinge](models/Hinge.stl){previewpage}, [trap latch](models/Trap_latch.stl){previewpage} and [groove pins](models/Grooved_pin.stl){previewpage}. Locate the holes on the lid and allign the hinge and latch then press fit the groove pins on the holes to fasten the latch and hinge on the clear sheet.

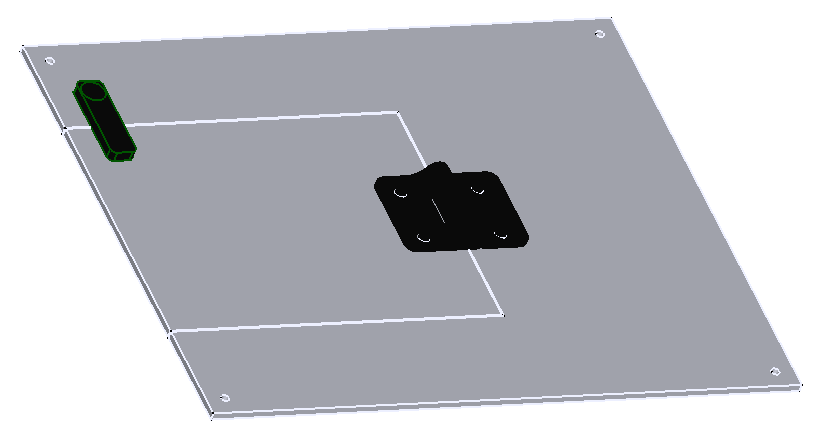
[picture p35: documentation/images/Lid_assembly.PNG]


+ Place the assembled lid on the box assembly. Then using [M3x8 Pozi pan machine screw]{Qty:4} fasten the lid tightening the screws using [Pozidriv PZ1 screw driver]{qty:1,cat:tool}.  

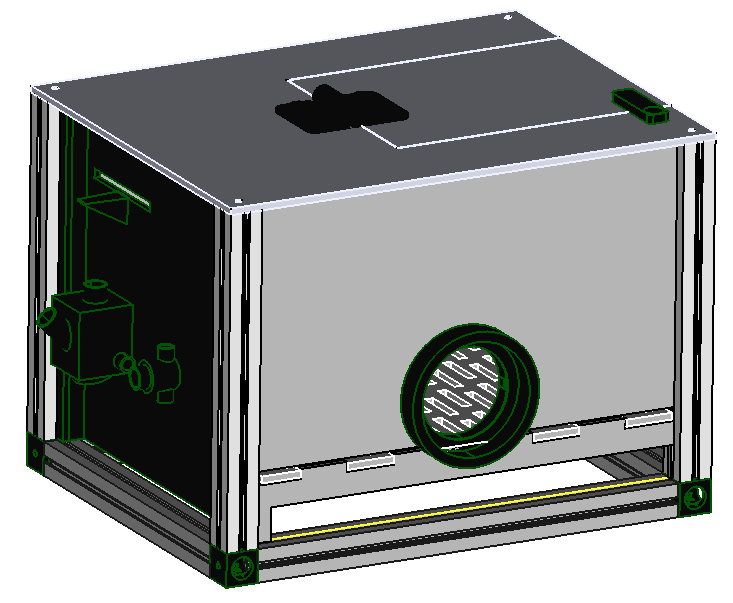
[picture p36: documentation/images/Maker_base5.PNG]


+ On the bottom of the box along the makerbeam xl groove slide the [guide rail](models/Guide_rail.svg) and make sure it is at the middle and fits tightly.

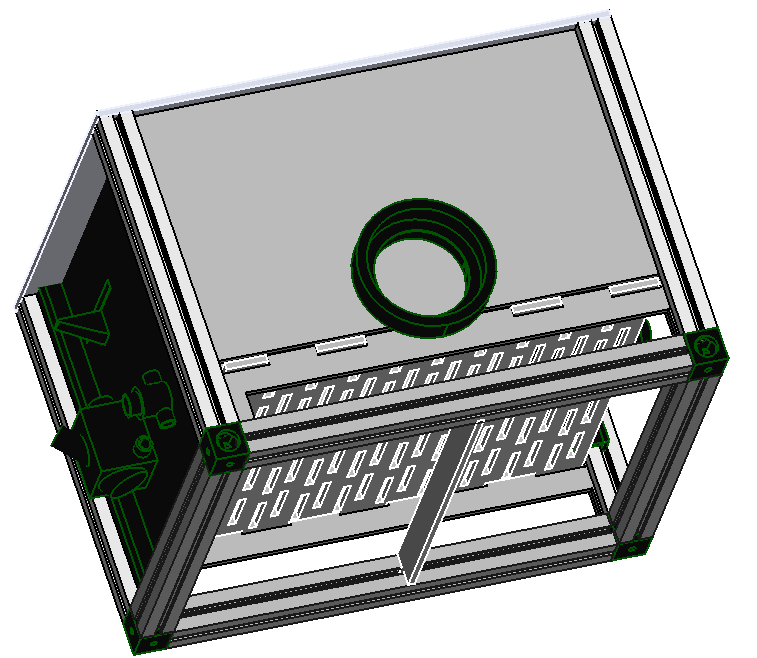
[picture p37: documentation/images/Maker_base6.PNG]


## Excrete panel{pagestep}

+ Using the Excrete box case parts [case back](models/Excrete_panel_RnL.svg), [case base](models/Excrete_panel_base.svg),[case front](models/Excrete_panel_RnL.svg), [case right](models/Excrete_panel_FnB.svg), [case left](models/Excrete_panel_FnB.svg) and [Liquid Adhesive]{Qty: 1 } stick the parts together and waith for them to dry.

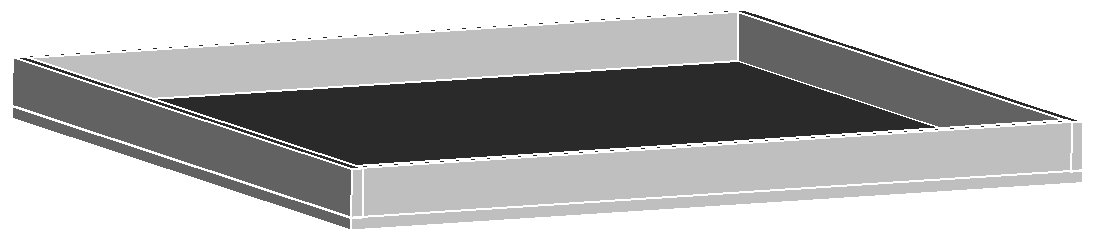
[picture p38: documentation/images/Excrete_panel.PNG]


## Putting things together{pagestep}

+ Place the box assembly on top of the electronics case and close the latches to make the assembly stable.

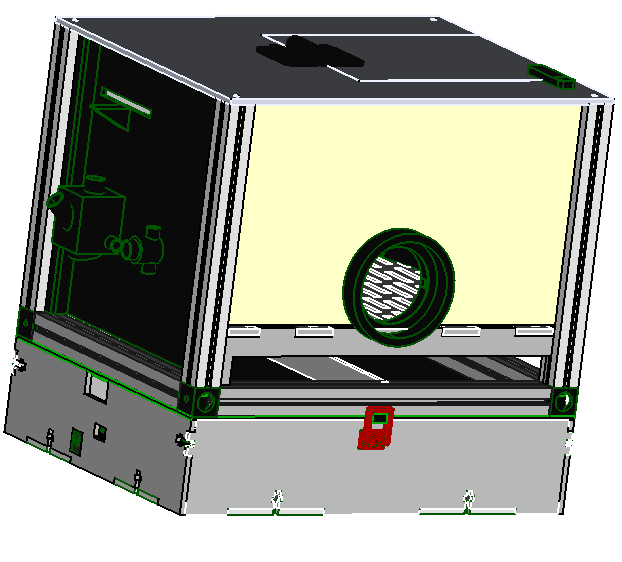
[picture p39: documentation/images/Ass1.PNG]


+ The assembled tray in should slid on the assembly in the assembly to make a collector for the animal excretion during experiment.



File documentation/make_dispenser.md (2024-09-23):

[Servo motor]:Parts.yaml#Servomotor
[clear plastic sheet]:Parts.yaml#ClearSheet
[2mm Hex key]:Parts.yaml#2mmHexkey
[Pozidriv PZ1 screw driver]:Parts.yaml#PozidrivPZ1
[M3x8mm hex socket counter sunk screw]:Parts.yaml#M3x8mmhexsocketcountersunk
[Flexible Tube]: Parts.yaml#Flexibletube

# Assembly Guide

{{BOM}}

## Motor holder {pagestep}

+ Push the [Servo motor]{qty: 1} on the 3d printed [motor holder](models/Motor_holder.stl){previewpage}.

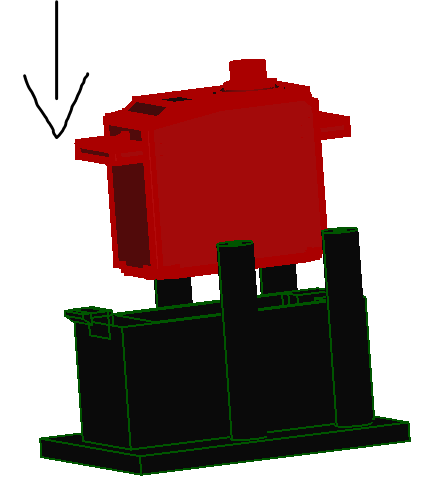
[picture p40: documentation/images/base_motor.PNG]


+ Align the motor holder pillars with the [tank base](models/base.stl){previewpage} holes and fasten the assembly using [M3x8mm hex socket counter sunk screw]{Qty:4} and use [2mm Hex key]{Qty:1, cat: tool} to tighten the screws. Make sure the smaller hole on the edge is in line with the servo motor wires

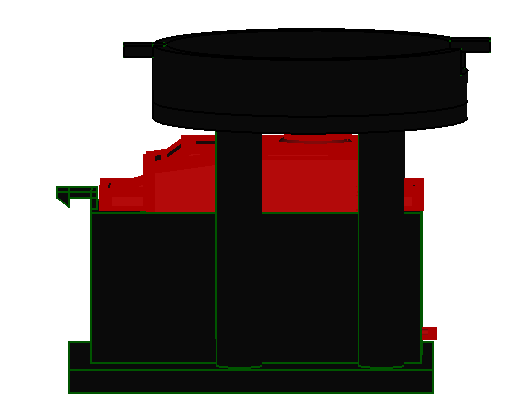
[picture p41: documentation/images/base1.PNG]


## Feed throat{pagestep}

+ Align the [Chute](models/chute_with_mount.stl){previewpage} with the two holes and the smaller hole on the tank base. Then fasten the feed throat with [M3x8mm hex socket counter sunk screw]{qty:2} and tighten uisng [Pozidriv PZ1 screw driver]{Qty: 1, cat: tool}.

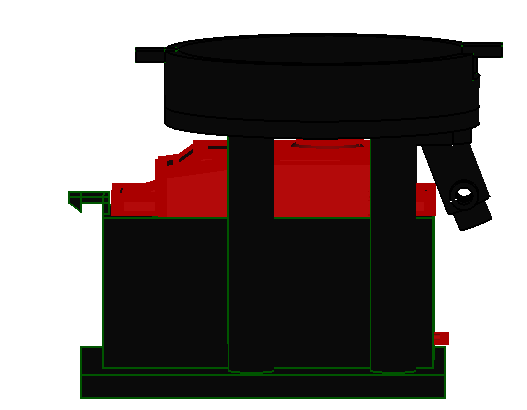
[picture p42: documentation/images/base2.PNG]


## Tank{pagestep}

+ Fit the [rotor](models/Rotor.stl){previewpage} on the servo motor shaft and fasten it using the [M3x8mm hex socket counter sunk screw]{Qty:1}.

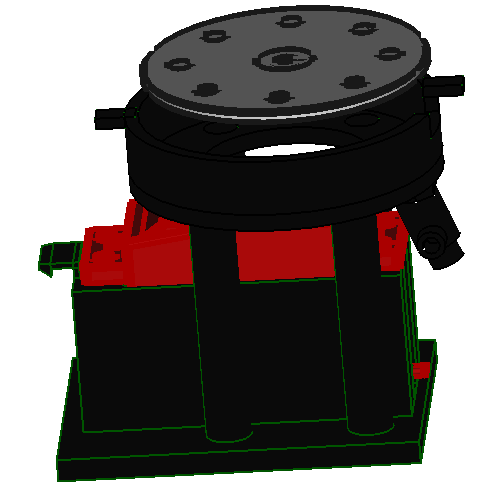
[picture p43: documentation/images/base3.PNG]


+ screw the [feed tank](models/Feed_tank.stl){previewpage} on to the tank base. Make sure the tabs fit in the slots.

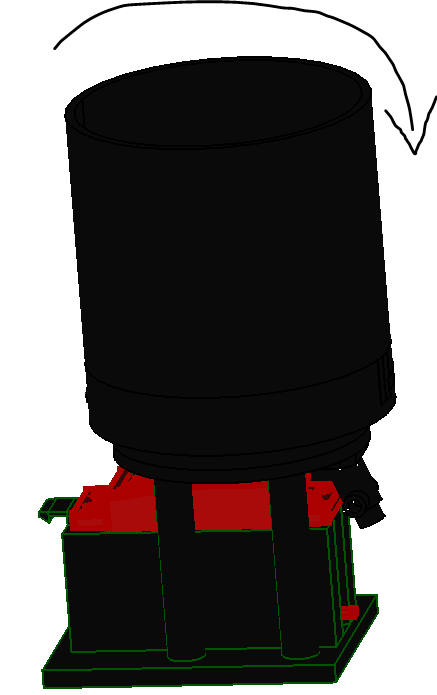
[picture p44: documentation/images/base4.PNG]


## Cover{pagestep}

+ Place the [outer cover](models/Outer_cover.svg) and [inner cover](models/Inner_cover.svg) on top of each other and align the holes with the [cover handle](models/Handle.stl){previewpage}. Then fasten them using the [M3x8mm hex socket counter sunk screw]{qty:1} on the cover handle hole.

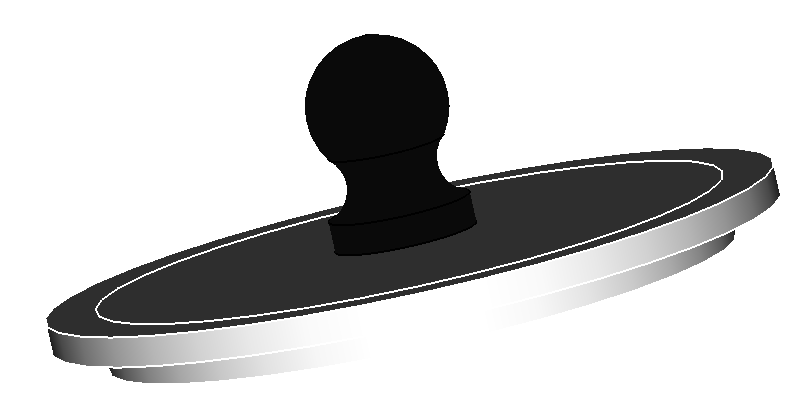
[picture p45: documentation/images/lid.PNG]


+ The lid can be placed ontop of the tank to cover the food. The [Flexible Tube]{qty:1, cat: material} is then press fit on the fed throat.

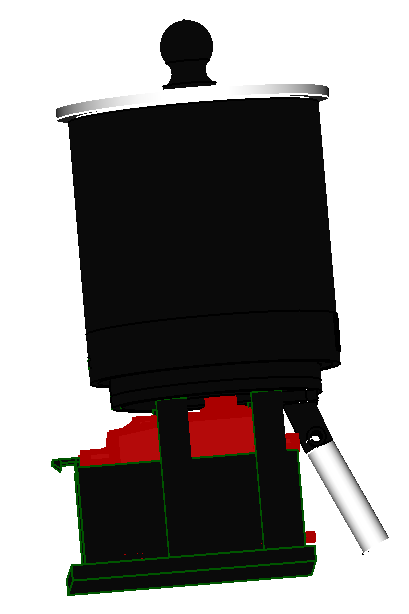
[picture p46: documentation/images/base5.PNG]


You made it!

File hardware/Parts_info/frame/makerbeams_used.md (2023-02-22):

#### List of Makerbeams used:
##### Makerbeam XL Black Starter Kit
*	2 x 200 mm beams
*	6 x 150 mm beams
*	2 x 100 mm beams
*	2 x T-bracket XL
*	18 x button head socket bolt M3, 6mm, A2
*	18 x M3 nut, A2
*	4 corner cubes

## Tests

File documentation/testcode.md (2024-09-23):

# Software

##Test LED{pagestep}
  - To test the [Led](testcode/Led_test.py)

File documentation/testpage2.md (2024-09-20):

[3d printer]:Parts.yaml#3dprinter
[Laser cutter]:Parts.yaml#Lasercutter
[PLA filament]:Parts.yaml#PLAfilament
[clear plastic sheet]:Parts.yaml#ClearSheet
[maker beam XL]:Parts.yaml#MakerBeamXL
[150mm mini hacksaw]:Parts.yaml#Hacksaw
[M3 tap set]:Parts.yaml#M3tapset
[tap wrench]:Parts.yaml#Tapwrench
[2mm Hex key]:Parts.yaml#2mmHexkey
[Pozidriv PZ1 screw driver]:Parts.yaml#PozidrivPZ1
[M3x8 Pozi pan machine screw]:Parts.yaml#M3X12mmPozipanscrews
[M3 hex Nut]:Parts.yaml#M3hexnut
[Liquid Adhesive]:Parts.yaml#Adhesive

# Reaction chamber


The chamber is used to track mice reaction time using light as a training cue. We will cover the step by step process of making the chamber in this section. 
>i [3d printer]{qty: 1, cat:machine} and  [Laser cutter]{qty: 1, cat:machine}  are OPTIONAL. If you dont have them you can outsource the services from your local supplier. 

{{BOM}}

>i If you have outsourced the printed and laser cut parts.  You migth need to inform your supplier to have  [PLA filament]{Qty: 400g, cat: material} for printing and [clear plastic sheet]{Qty: 1, cat: material} for laser cutting.

## Electronics box{pagestep}
 + Using a laser cutter, cut the following parts:
     + 1 pc of [Ecase_Back](models/Ecase_Back.svg)
     + 1 pc of [Ecase_Base](models/Ecase_Base.svg)
     + 1 pc of [Ecase_Front](models/Ecase_Front.svg)
     +  2 pcs of [Ecase_R&L](models/Ecase_RnL.svg)

   + Assemble the Electronics box with the laser cut parts to form a box then fasten the box with [M3 hex Nut]{Qty:12} and  [M3x8 Pozi pan machine screw]{Qty:12} using [Pozidriv PZ1 screw driver]{qty:1,cat:tool} to tighten the nuts.



## Electronics board{pagestep}

   + Position the Pcb board in line with the holes on the side of the box assembly. Then using  [M3x8 Pozi pan machine screw]{Qty:4}fasten the board using  [Pozidriv PZ1 screw driver]{qty:1,cat:tool} to tighten the screws.



## Electronics cover{pagestep}

  + Print the two models below
 



>! Do not print the latch_assembly.stl as one part 

   + Snap fit the latch_handle.svg on to the latch_base.svg part to from the [Latch_assembly](models/Latch_assembly.stl){previewpage}.

 + Locate the holes on the side of the box and using [M3 hex Nut]{Qty:2} and [M3x8 Pozi pan machine screw]{Qty:2} fasten the assembled latch to the box uisng [Pozidriv PZ1 screw driver]{qty:1,cat:tool}.   

   

 + Place the [Electronics top](models/Electronics_top.stl){previewpage} on top of the box and fasten it using the latch assembly.



## Maker beam frame{pagestep}

 + Using [150mm mini hacksaw]{Qty:1,cat: Tool} cut 2 pcs 200mm long and 6 pcs 150mm long from the [maker beam XL]{Qty:1,cat: material}
 
  + From the [M3 tap set]{Qty:1,cat: Tool} place the taping screw on the [tap wrench]{Qty:1,cat: Tool} then make threads on the holes at the end of the maker beam xl pieces that you had cut ealier. 

  + Place 2 makerbeam xl 200mm and 150 mm end to end at their meeting point joing them together using [corner](models/corner.stl){previewpage}. to make a square frame. Using [M3x8 Pozi pan machine screw]{Qty:12} fasten the corners to the maker beam xl uisng [Pozidriv PZ1 screw driver]{qty:1,cat:tool}. Repeat the process for all the corners to make a rectangle.

  

  + At the corners of the square frame fasten horizontally 4 more maker beam xl using [M3x8 Pozi pan machine screw]{Qty:4}.  



## Adding the enclosure{pagestep}

 + Slide the [platform support](models/Platform_support.svg) parts on opposite sides of the pillars and on top of them place the [Platform base](models/Platform_base.svg).



 + Slide the [feeding wall](models/Feeding_wall.stl){previewpage} making sure it goes all the way to the bottom. Then for the [led series wall](models/Led_series_wall.stl){previewpage} will slide up to the platform and on top of it slide the [curved wall](models/Curved_wall.stl){previewpage}.
.


+ With the [side entry wall](models/Side_entry_wall.svg) press fit the [tunnel connector](models/Tunnel_connector.stl){previewpage} and the [tunnel clamp](models/Tunnel_clamp.stl){previewpage} on either side of the plasric sheet.



+ Slide the [side entry wall](models/Side_entry_wall.svg) and the [side plain wall](models/Side_plain_wall.svg) through the pillars of the box.



+ With the [lid](models/Lid.svg) pieces, [hinge](models/Hinge.stl){previewpage}, [trap latch](models/Trap_latch.stl){previewpage} and [groove pins](models/Grooved_pin.stl){previewpage}. Locate the holes on the lid and allign the hinge and latch then press fit the groove pins on the holes to fasten the latch and hinge on the clear sheet.



+ Place the assembled lid on the box assembly. Then using [M3x8 Pozi pan machine screw]{Qty:4} fasten the lid tightening the screws using [Pozidriv PZ1 screw driver]{qty:1,cat:tool}.  



+ On the bottom of the box along the makerbeam xl groove slide the [guide rail](models/Guide_rail.svg) and make sure it is at the middle and fits tightly.



## Excrete panel{pagestep}

+ Using the Excrete box case parts [case back](models/Excrete_panel_RnL.svg), [case base](models/Excrete_panel_base.svg),[case front](models/Excrete_panel_RnL.svg), [case right](models/Excrete_panel_FnB.svg), [case left](models/Excrete_panel_FnB.svg) and [Liquid Adhesive]{Qty: 1 } stick the parts together and waith for them to dry.



## Putting things together{pagestep}

+ Place the box assembly on top of the electronics case and close the latches to make the assembly stable.



+ The assembled tray in should slid on the assembly in the assembly to make a collector for the animal excretion during experiment.



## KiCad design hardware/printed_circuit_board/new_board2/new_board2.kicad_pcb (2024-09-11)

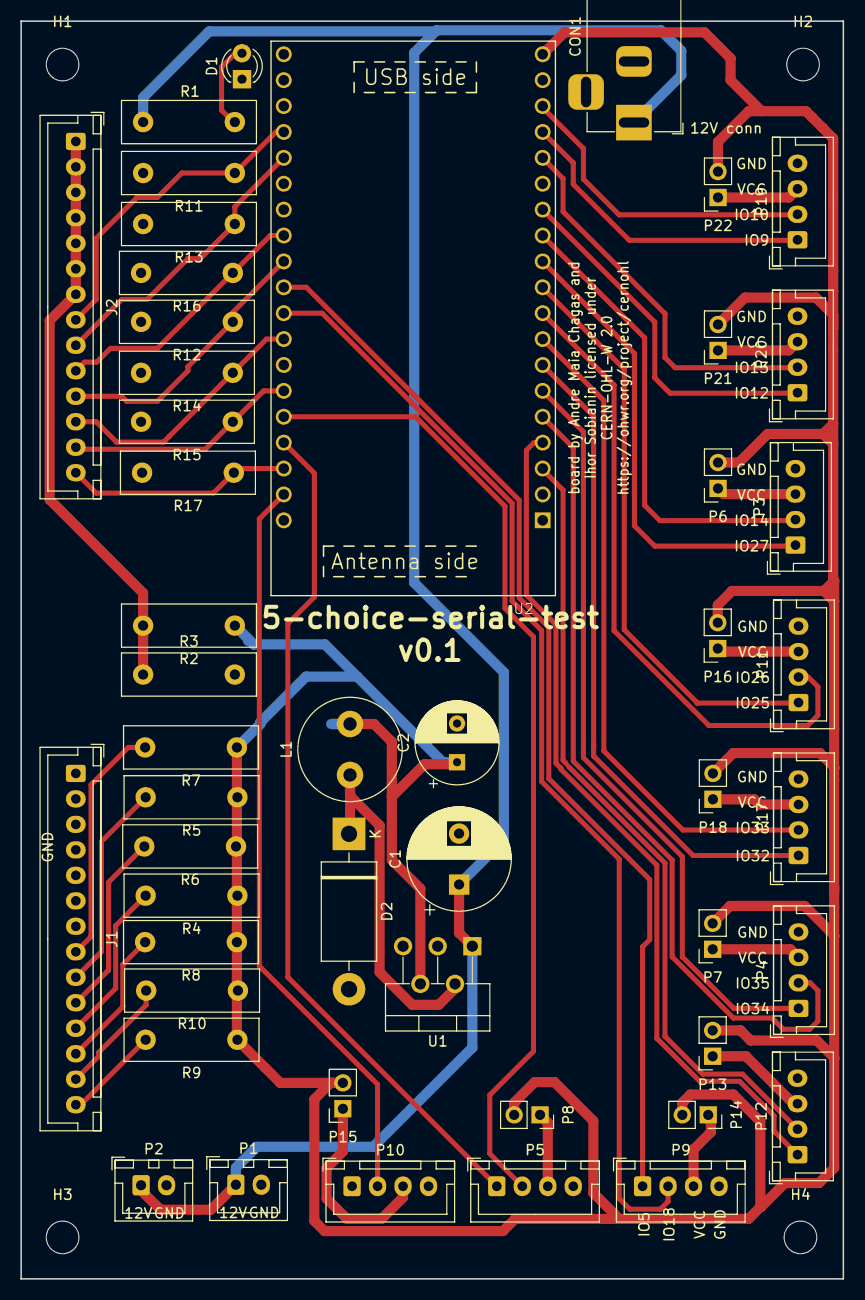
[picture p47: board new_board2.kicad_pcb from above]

Board: 2 copper layers, 80.7 x 123.4 mm, 53 parts (0 on the bottom side), 49 nets.

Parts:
C1: 680µ; CP_Radial_D10.0mm_P5.00mm
C2: 220µ; CP_Radial_D8.0mm_P3.80mm
CON1: BARREL_JACK; BarrelJack_Horizontal
D1: LED; LED_D3.0mm
D2: Schottky 5A; D_DO-201AD_P15.24mm_Horizontal
H1, H2, H3, H4: MountingHole; MountingHole_3.2mm_M3
J1, J2: Conn_01x14_Socket; JST_XH_B14B-XH-A_1x14_P2.50mm_Vertical
L1: 33µH; L_Radial_D10.0mm_P5.00mm_Fastron_07M
P1, P2: Conn_01x02; JST_XH_B2B-XH-A_1x02_P2.50mm_Vertical
P3: D7; JST_XH_B4B-XH-A_1x04_P2.50mm_Vertical
P4: A1; JST_XH_B4B-XH-A_1x04_P2.50mm_Vertical
P5: UART; JST_XH_B4B-XH-A_1x04_P2.50mm_Vertical
P6, P7, P8, P13, P14, P15, P16, P18, P21, P22: Conn_01x02; PinSocket_1x02_P2.54mm_Vertical
P9: D4; JST_XH_B4B-XH-A_1x04_P2.50mm_Vertical
P10: D6; JST_XH_B4B-XH-A_1x04_P2.50mm_Vertical
P11: D8; JST_XH_B4B-XH-A_1x04_P2.50mm_Vertical
P12: A2; JST_XH_B4B-XH-A_1x04_P2.50mm_Vertical
P17: A3; JST_XH_B4B-XH-A_1x04_P2.50mm_Vertical
P19: I2C 1; JST_XH_B4B-XH-A_1x04_P2.50mm_Vertical
P20: I2C 2; JST_XH_B4B-XH-A_1x04_P2.50mm_Vertical
R1, R2: 560; R_Box_L13.0mm_W4.0mm_P9.00mm
R3: 1k; R_Box_L13.0mm_W4.0mm_P9.00mm
R4, R5, R6, R7, R8, R9, R10: 47; R_Box_L13.0mm_W4.0mm_P9.00mm
R11, R12, R13, R14, R15, R16, R17: 10k; R_Box_L13.0mm_W4.0mm_P9.00mm
U1: LM2596T-5; TO-220-5_P3.4x3.7mm_StaggerOdd_Lead3.8mm_Vertical
U2: ESP32-DEVKITC-32D; MODULE_ESP32-DEVKITC-32D

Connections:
+3V3: J2.1, J2.2, J2.3, J2.4, J2.5, J2.6, J2.7, R2.2, R3.1
+5V: C2.1, L1.2, P6.2, P7.2, P8.2, P13.2, P14.2, P15.2, P16.2, P18.2, P21.2, P22.2, R2.1, R4.1, R5.1, R6.1, R7.1, R8.1, R9.1, R10.1, U1.4 (FB), U2.19 (EXT_5V)
+12V: C1.1, CON1.1, P1.1, P2.1, R1.2, U1.1 (VIN)
A1-3: P4.1, U2.6 (IO35)
A1-4: P4.2, U2.5 (IO34)
A2-3: P12.1, U2.4 (SENSOR_VN)
A2-4: P12.2, U2.3 (SENSOR_VP)
A3-3: P17.1, U2.7 (IO32)
A3-4: P17.2, U2.8 (IO33)
D1-3: J2.8, R11.1, U2.35 (IO15)
D1-4: J2.9, R13.1, U2.34 (IO2)
D3-3: J2.10, R16.1, U2.31 (IO16)
D3-4: J2.11, R12.1, U2.30 (IO17)
D4-3: P9.1, U2.29 (IO5)
D4-4: P9.2, U2.28 (IO18)
D5-3: J2.12, R14.1, U2.27 (IO19)
D5-4: J2.13, R15.1, U2.25 (IO21)
D6-3: J2.14, R17.1, U2.22 (IO22)
D6-4: P10.2, U2.21 (IO23)
D7-3: P3.1, U2.12 (IO14)
D7-4: P3.2, U2.11 (IO27)
D8-3: P11.1, U2.10 (IO26)
D8-4: P11.2, U2.9 (IO25)
GND: C1.2, C2.2, CON1.2, CON1.3, D1.1 (K), D2.2 (A), J1.1, J1.2, J1.3, J1.4, J1.5, J1.6, J1.7, P1.2, P2.2, P3.4, P4.4, P5.4, P9.4, P10.4, P11.4, P12.4, P17.4, P19.4, P20.4, R3.2, R11.2, R12.2, R13.2, R14.2, R15.2, R16.2, R17.2, U1.3 (GND), U1.5 (~ON/OFF), U2.14 (GND1), U2.20 (GND3), U2.26 (GND2)
I2C_1-3: P19.1, U2.16 (SD2)
I2C_1-4: P19.2, U2.17 (SD3)
I2C_2-3: P20.1, U2.13 (IO12)
I2C_2-4: P20.2, U2.15 (IO13)
unnamed: D1.2 (A), R1.1
unnamed: D2.1 (K), L1.1, U1.2 (OUT)
unnamed: J1.8, R7.2
unnamed: J1.9, R5.2
unnamed: J1.10, R6.2
unnamed: J1.11, R4.2
unnamed: J1.12, R8.2
unnamed: J1.13, R10.2
unnamed: J1.14, R9.2
unnamed: P3.3, P6.1
unnamed: P4.3, P7.1
unnamed: P5.3, P8.1
unnamed: P10.3, P15.1
unnamed: P11.3, P16.1
unnamed: P12.3, P13.1
unnamed: P9.3, P14.1
unnamed: P17.3, P18.1
unnamed: P19.3, P22.1
unnamed: P20.3, P21.1
RX: P5.2, U2.24 (RXD0)
TX: P5.1, U2.23 (TXD0)

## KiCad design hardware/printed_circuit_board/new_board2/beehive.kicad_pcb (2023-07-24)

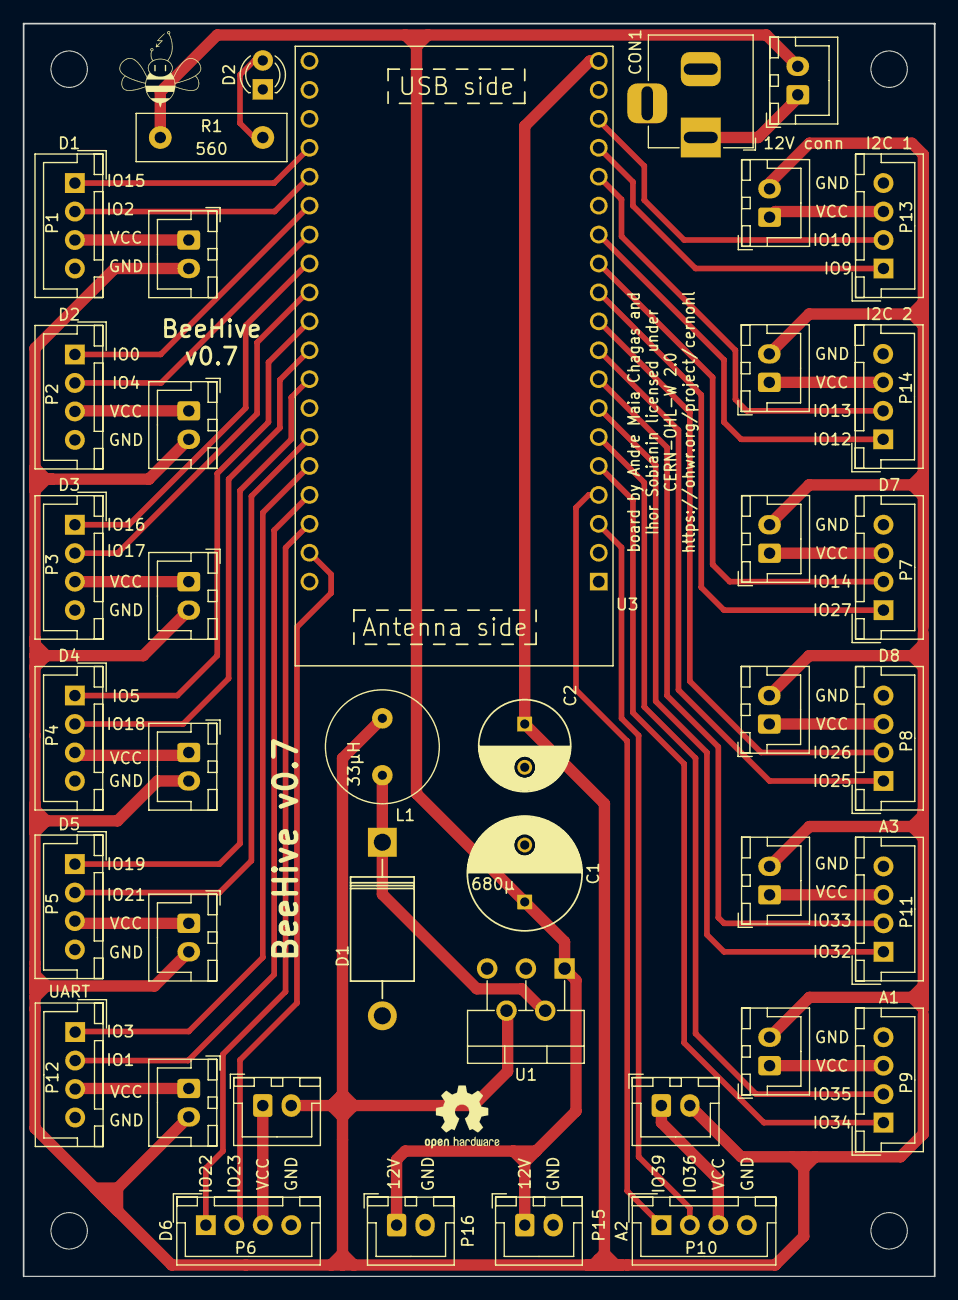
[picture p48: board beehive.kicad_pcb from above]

Board: 2 copper layers, 80.0 x 110.0 mm, 41 parts (0 on the bottom side), 48 nets.

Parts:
 : OSHW-Logo2_7.3x6mm_SilkScreen
C1: 680µ; C_Radial_D10_L21_P5
C2: 220µ; C_Radial_D8_L13_P3.8
CON1: BARREL_JACK; BarrelJack_Horizontal
D1: Schottky 5A; Diode_DO-201AD_Horizontal_RM15
D2: LED; LED_D3.0mm
L1: 33µH; Neosid_Inductor_MA-Bs75
P1: D1; JST_XH_B04B-XH-A_04x2.50mm_Straight
P2: D2; JST_XH_B04B-XH-A_04x2.50mm_Straight
P3: D3; JST_XH_B04B-XH-A_04x2.50mm_Straight
P4: D4; JST_XH_B04B-XH-A_04x2.50mm_Straight
P5: D5; JST_XH_B04B-XH-A_04x2.50mm_Straight
P6: D6; JST_XH_B04B-XH-A_04x2.50mm_Straight
P7: D7; JST_XH_B04B-XH-A_04x2.50mm_Straight
P8: D8; JST_XH_B04B-XH-A_04x2.50mm_Straight
P9: A1; JST_XH_B04B-XH-A_04x2.50mm_Straight
P10: A2; JST_XH_B04B-XH-A_04x2.50mm_Straight
P11: A3; JST_XH_B04B-XH-A_04x2.50mm_Straight
P12: UART; JST_XH_B04B-XH-A_04x2.50mm_Straight
P13: I2C 1; JST_XH_B04B-XH-A_04x2.50mm_Straight
P14: I2C 2; JST_XH_B04B-XH-A_04x2.50mm_Straight
P15, P16, P17, P18, P19, P20, P21, P22, P23, P24, P25, P26, P27, P28, P29, P30, P31: Conn_01x02; JST_XH_B2B-XH-A_1x02_P2.50mm_Vertical
R1: 560; R_Box_L13.0mm_W4.0mm_P9.00mm
U1: LM2596T-5; TO-220-5_P3.4x3.7mm_StaggerOdd_Lead3.8mm_Vertical
U3: ESP32-DEVKITC-32D; MODULE_ESP32-DEVKITC-32D

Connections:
+5V: C2.1, L1.2, P17.2, P18.2, P19.2, P20.2, P21.2, P22.2, P23.2, P24.2, P25.2, P26.2, P27.2, P28.2, P29.2, P30.2, U1.4 (FB), U3.19 (EXT_5V)
A1-3: P9.2, U3.6 (IO35)
A1-4: P9.1, U3.5 (IO34)
A2-3: P10.1, U3.4 (SENSOR_VN)
A2-4: P10.2, U3.3 (SENSOR_VP)
A3-3: P11.1, U3.7 (IO32)
A3-4: P11.2, U3.8 (IO33)
D1-3: P1.1, U3.35 (IO15)
D1-4: P1.2, U3.34 (IO2)
D2-3: P2.1, U3.33 (IO0)
D2-4: P2.2, U3.32 (IO4)
D3-3: P3.1, U3.31 (IO16)
D3-4: P3.2, U3.30 (IO17)
D4-3: P4.1, U3.29 (IO5)
D4-4: P4.2, U3.28 (IO18)
D5-3: P5.1, U3.27 (IO19)
D5-4: P5.2, U3.25 (IO21)
D6-3: P6.1, U3.22 (IO22)
D6-4: P6.2, U3.21 (IO23)
D7-3: P7.1, U3.11 (IO27)
D7-4: P7.2, U3.12 (IO14)
D8-3: P8.2, U3.10 (IO26)
D8-4: P8.1, U3.9 (IO25)
GND: C1.2, C2.2, CON1.2, CON1.3, D1.2 (A), D2.1 (K), P1.4, P2.4, P3.4, P4.4, P5.4, P6.4, P7.4, P8.4, P9.4, P10.4, P11.4, P12.4, P13.4, P14.4, P15.2, P16.2, U1.3 (GND), U1.5 (~ON/OFF), U3.14 (GND1), U3.20 (GND3), U3.26 (GND2)
I2C_1-3: P13.1, U3.16 (SD2)
I2C_1-4: P13.2, U3.17 (SD3)
I2C_2-3: P14.1, U3.13 (IO12)
I2C_2-4: P14.2, U3.15 (IO13)
unnamed: C1.1, P15.1, P16.1, P31.2, R1.2, U1.1 (VIN)
unnamed: CON1.1, P31.1
unnamed: D1.1 (K), L1.1, U1.2 (OUT)
unnamed: D2.2 (A), R1.1
unnamed: P1.3, P17.1
unnamed: P2.3, P23.1
unnamed: P10.3, P27.1
unnamed: P11.3, P28.1
unnamed: P12.3, P21.1
unnamed: P13.3, P29.1
unnamed: P14.3, P30.1
unnamed: P3.3, P18.1
unnamed: P5.3, P19.1
unnamed: P7.3, P20.1
unnamed: P9.3, P22.1
unnamed: P4.3, P24.1
unnamed: P6.3, P25.1
unnamed: P8.3, P26.1
RX: P12.1, U3.24 (RXD0)
TX: P12.2, U3.23 (TXD0)

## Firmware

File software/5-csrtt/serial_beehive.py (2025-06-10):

# These are imports necessary to use the belay library
import belay
from belay import Device
import time
#import utime




class SerialBeeHive(Device): #This is the class that contains all the phases 
    
    @Device.setup # Device setup is where the yellow LEDs and sensor LEDs are defined, also imports.
    def setup():

        #these imports are necessary for the different phases
        import machine
        import time 
        import random
        import utime

        #This is for the stepper motor that turns the food dispenser allowing
        #from machine import Pin
        #from machine import PWM
        from machine import ADC
        


        
        #The pins for the servo motor on the pellet dispenser
        dispenser_motor = machine.PWM(Pin(18),freq =50)


        #pins = [IN1, IN2, IN3, IN4]
        magazine_sensor_pin = 15
        dispenser_sensor_pin = 39
        trial_start_sensor_pin = 2
        
        

        magazine_sensor = machine.Pin(magazine_sensor_pin,machine.Pin.IN) # Sensor LED for the food magazine
        dispenser_sensor = machine.Pin(dispenser_sensor_pin, machine.Pin.IN) # Sensor LEDs for the food dispenser to detect when food pellets come down
        trial_start_sensor = machine.Pin(trial_start_sensor_pin, machine.Pin.IN) # Sensor for trial start light
        
        
        food_led = machine.Pin(33, machine.Pin.OUT) #LED = the yellow LED for the food magazine
        
        #All the pins for teh yellow LEDs nose pokes
        nose_poke_led_1 = machine.Pin(14,machine.Pin.OUT) 
        nose_poke_led_2 = machine.Pin(27,machine.Pin.OUT)
        nose_poke_led_3 = machine.Pin(25,machine.Pin.OUT)
        nose_poke_led_4 = machine.Pin(26, machine.Pin.OUT)
        nose_poke_led_5 = machine.Pin(32,machine.Pin.OUT)

        #All the IR. sensors for the different Nose pokes
        nose_poke_sensor_1 = machine.Pin(16,machine.Pin.IN)
        nose_poke_sensor2 = machine.Pin(17,machine.Pin.IN) 
        nose_poke_sensor3 = machine.Pin(19,machine.Pin.IN)
        nose_poke_sensor4 = machine.Pin(21,machine.Pin.IN)
        nose_poke_sensor5 = machine.Pin(22,machine.Pin.IN)
        

        
        #This is to associate each button with the Nose poke for the data output on the excel sheet
        np_sensor_correspondence = [ (nose_poke_sensor1, "nose_poke_led_1"), (nose_poke_sensor2, "nose_poke_led_2"), (nose_poke_sensor3, "nose_poke_led_3"), (nose_poke_sensor4, "nose_poke_led_4"), (nose_poke_sensor5,"nose_poke_led_5")]


        #This sets all the Nosepoked yellow LED values at 0 before the trial starts
        nose_poke_led_1.value(0)
        nose_poke_led_2.value(0)
        nose_poke_led_3.value(0)
        nose_poke_led_4.value(0)
        nose_poke_led_5.value(0)
        
        def count_time(interval):
            timer1 = time.ticks_ms()
            timer2 = time.ticks_ms()
            while timer2-timer1<=interval:
                timer2=time.ticks_ms()
            
            return timer2-timer1
            
        #This is the function for the food dispenser giving the reward:
        
        def reward():
            pellet_dropped = 0 #Pellet is one which allows for the food dispensing to start through the while loop underneath
            reward_servo_mov_time = 800;
            

            while pellet_dropped==0:
                dispenser_motor.duty(50)
                timer1 = time.ticks_ms()
                timer2 = time.ticks_ms()
                while(timer2-timer1<reward_servo_mov_time):
                    pellet = dispenser_sensor.value()
                    #print(pellet)
                    timer2 = time.ticks_ms()
                    if pellet == 0:
                        pellet_dropped = 1
                        break
                
                if pellet_dropped == 0:
                    dispenser_motor.duty(23)
                    timer1 = time.ticks_ms()
                    timer2 = time.ticks_ms()
                    while(timer2-timer1<reward_servo_mov_time):
                        timer2 = time.ticks_ms()
                        pellet = dispenser_sensor.value()     
                        if pellet == 0:
                            pellet_dropped = 1
                            break
        
    @Device.task 
    def food_training(num_trial=50): #this is the function for the food training
        """Food magazine training"""
        
        total=time.ticks_ms()
       


        for trial in range (num_trial): #trials meaning trials that can be changed in the brackets
          
            start_trial_time= time.ticks_ms() #this is a timer of the start of the trial -> gives number in miliseconds not actual time   


            food_led.value(1) #the food magazine LED value starts at 0
            reward() 
            #food_led.value(0)# once the mouse went for the food, the while loop stops and the food magazine yellow LED turns off

            
            timer_food = time.ticks_ms()# timer starts to know when the mouse went for the food
            timer_food2 = time.ticks_ms()
            #print(magazine_sensor.value())
            while magazine_sensor.value() == 1:#while the food magazine sensor LEDs are 1 that means there has been no interruption. This means the mouse hasn't reached for the food
                utime.sleep(0.1)
                timer_food2=time.ticks_ms() # as soon as the magazine_sensor.value(1), it starts counting          
            food_led.value(0)# once the mouse went for the food, the while loop stops and the food magazine yellow LED turns off
            
            #ITIs
            times=[4,8,16,32] 
            
            times_num = random.choice(times) #one random time out of these is chosen
            #times_num = times_num*1000 #convert seconds to milliseconds
            count_time(times_num) # time.sleeps allows for the machine to pause for the amount of times the ITI is
            
            
            mouse_to_food = timer_food2-timer_food #mouse to food is the amount of time the mouse took to get the food
            end_trial_time = time.ticks_ms()
            
            trial_duration = end_trial_time-start_trial_time #end of the whole task
            
            timer_end = utime.ticks_ms()
            total_time=timer_end-total # end of the whole task
            
    
            
            yield([trial+1, times_num, start_trial_time, mouse_to_food, trial_duration, total_time])  #variables that are going to be yielded into the CSV file

    @Device.task
    def phase1():
        
        """Phase 1"""
        
        total=time.ticks_ms()
        
        for trial in range (50):
            
            start_trial_time= time.ticks_ms() #this is a timer of the start of the trial -> gives number in miliseconds not actual time   
            food_led.value(1) #the food magazine LED value starts at 0
            
            while trial_start_sensor.value() == 1:#while the food magazine sensor LEDs are 1 that means there has been no interruption. This means the mouse hasn't reached for the food
                print(trial_start_sensor.value())
                utime.sleep(0.5)
               
            food_led.value(0)# once the mouse went for the food, the while loop stops and the food magazine yellow LED turns off
            reward()
            
            timer_food = time.ticks_ms()# timer starts to know when the mouse went for the food
            
            while magazine_sensor.value() == 1:#while the food magazine sensor LEDs are 1 that means there has been no interruption. This means the mouse hasn't reached for the food
                
                utime.sleep(0.1)
                timer_food2=time.ticks_ms() # as soon as the magazine_sensor.value(1), it starts counting  
            food_led.value(0) #the food magazine LED value starts at 0 
            
            mouse_to_food = timer_food2-timer_food #mouse to food is the amount of time the mouse took to get teh food
            end_trial_time = time.ticks_ms()

            trial_duration = end_trial_time-start_trial_time #end of the whole task

            timer_end = utime.ticks_ms()
            total_time=timer_end-total # end of the whole task

            yield([trial+1,start_trial_time, mouse_to_food, trial_duration, total_time])  #variables that are going to be yielded into the CSV file

    @Device.task
    def phase2():
        
        """Phase 2"""
        total=time.ticks_ms()
        
        for trial in range (50):
            
            start_trial_time= time.ticks_ms() #this is a timer of the start of the trial    
            food_led.value(1) #the food magazine LED value starts at 0
            
            while trial_start_sensor.value() == 1:#while the food magazine sensor LEDs are 1 that means there has been no interruption. This means the mouse hasn't reached for the food
                print(trial_start_sensor.value())
                utime.sleep(0.5)          
            food_led.value(0)# once the mouse went for the food, the while loop stops and the food magazine yellow LED turns off
            
            button_pressed = False
            
            while button_pressed== False: #this a while loop that allows for the conditions 
    
                #if any of the buttons are interrupted the sensor will go from 1 to 0 showing an interruption
                #Here one of the Nosepokes has been poked
                if nose_poke_sensor1.value() == 0 or nose_poke_sensor2.value() == 0  or nose_poke_sensor3.value() == 0  or nose_poke_sensor4.value() == 0 or nose_poke_sensor5.value()==0: #if any of the NPs are poked
                      
                    #Lights are turned off
                    nose_poke_led_1.value(0) 
                    nose_poke_led_2.value(0)
                    nose_poke_led_3.value(0)
                    nose_poke_led_4.value(0)
                    nose_poke_led_5.value(0)
                    
                    #Reward is sent
                    reward()
                    
                    timer_food = time.ticks_ms()

                    while magazine_sensor.value() == 1:
                        timer_food2 = time.ticks_ms()
                        
                    mouse_to_food = timer_food2-timer_food
                    
                    button_pressed = True #when the button pressed is true then the while loop can stop and the trial can go again
                    
                    trial_end = time.ticks_ms()
                    trial_duration = trial_end-start_trial_time
                           
                #If no NPs are pressed then nothing happens
                elif nose_poke_sensor1.value() == 1 or nose_poke_sensor2.value() == 1 or nose_poke_sensor3.value() == 1 or nose_poke_sensor4.value() == 1 or nose_poke_sensor5.value() == 1:#0 meaning the NPs haven't been touched     
                        nose_poke_led_1.value(1) #THE Lights remain on
                        nose_poke_led_2.value(1)
                        nose_poke_led_3.value(1)
                        nose_poke_led_4.value(1)
                        nose_poke_led_5.value(1)
                        food_led.value(0)
                        
            timer_end = utime.ticks_ms()
            total_time=timer_end-total # end of the whole task
            
            #yield([trial+1, mouse_to_food, start_trial_time,trial_duration])   
            yield([trial+1, start_trial_time, mouse_to_food, trial_duration, total_time])
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

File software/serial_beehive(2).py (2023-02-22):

# These are imports necessary to use the belay library
import belay
from belay import Device
import time




class SerialBeeHive(Device): #This is the class that contains all the phases 
    
    @Device.setup # Device setup is where the yellow LEDs and sensor LEDs are defined, also imports.
    def setup():

        #these imports are necessary for the different phases
        import machine
        import utime 
        import random
        

        #This is for the stepper motor that turns the food dispenser allowing
        from machine import Pin  
        from time import sleep

        
        #The pins from the stepper motor
        IN1 = machine.Pin(27,machine.Pin.OUT)
        IN2 = machine.Pin(14,machine.Pin.OUT)
        IN3 =machine.Pin(25,machine.Pin.OUT)
        IN4 =machine.Pin(26,machine.Pin.OUT)

        pins = [IN1, IN2, IN3, IN4]


        led=machine.Pin(15, machine.Pin.OUT) #LED = the yellow LED for the food magazine
        button_food=machine.Pin(22,Pin.IN) # Seonsr LED fro teh food magazine
        button_dispenser = machine.Pin(35, machine.Pin.IN) # Sensor LEDs for the food dispenser to detect when food pellets come down

        #All the pins for teh yellow LEDs nose pokes
        NP_1=machine.Pin(17,machine.Pin.OUT) 
        NP_2=machine.Pin(16,machine.Pin.OUT)
        NP_3=machine.Pin(19,machine.Pin.OUT)
        NP_4=machine.Pin(21, machine.Pin.OUT)
        NP_5=machine.Pin(2,machine.Pin.OUT)

        #All the IR. sensors for the different Nose pokes
        button_1 = machine.Pin(23,Pin.IN)
        button_2 = machine.Pin(5,Pin.IN) 
        button_3 = machine.Pin(18,Pin.IN)
        button_4 = machine.Pin(4,Pin.IN)
        button_5 = machine.Pin(32,machine.Pin.IN)
        

        
        #This is to associate each button with the Nose poke for the data output on teh excel sheet
        button_correspondance = [ (button_1, "NP_1"), (button_2, "NP_2"), (button_3, "NP_3"), (button_4, "NP_4"), (button_5,"NP_5")]
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

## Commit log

2022-11-28 put together an adaptor for the food hopper
    quick and dirt adaptation from an existing OSH project to use our existing motors
    [28BYJ-48 5V Stepper Motor.stp, SG90 Servo.STEP, food_hopper_assembly.FCStd, food_hopper_assembly.amf]
2022-11-29 first working version?
    [food_hopper_assembly-base_n_motor_holder.amf]
2023-01-09 update 3d printed components
    [food_hopper_assembly-motor_base.amf, nose_poke.stl]
2023-01-18 work on designs
    [food_hopper_assembly-rotor_final.amf, rotor_holes_template.scad, rotor_holes_template.stl]
2023-01-19 update rotor
    [rotor_holes_template.scad, rotor_holes_template.stl]
2023-01-19 rework food well
    [magazine.scad]
2023-01-19 work on 3D designs
    [Unnamed1-Cut.amf, bae_in_case_needed.scad, base.stl, magazine.scad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]
2023-01-20 Python code to run 5CSRTT
    [mouse1_Food_magazine_training_19_01_2023-15_18_42.csv, mouse1_Food_magazine_training_19_01_2023-15_19_42.csv, mouse1_Food_magazine_training_19_01_2023-15_19_57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]
2023-01-22 updated serial beehive
    [mouse1_Food_magazine_training_19_01_2023-15_18_42.csv, mouse1_Food_magazine_training_19_01_2023-15_19_42.csv, mouse1_Food_magazine_training_19_01_2023-15_19_57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]
2023-01-24 5csrtt modifications
    [mouse1_Food_magazine_training_24_01_2023-05_50_09.csv, mouse1_Food_magazine_training_24_01_2023-05_53_37.csv, mouse1_Food_magazine_training_24_01_2023-05_55_46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]
2023-02-10 code change 5CSRTT
    [mouse1_Food_magazine_training_20_01_2023-16_50_37.csv, mouse1_Food_magazine_training_24_01_2023-05_50_09.csv, mouse1_Food_magazine_training_24_01_2023-05_53_37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]
2023-02-22 repo clean up nd some code clean up
    [mouse1_Food_magazine_training_20_01_2023-16_50_37.csv]
2023-02-27 back panel
    [backpanel.scad, nosepoke_back.scad]
2023-02-27 small cleanups
    [backpanel.scad, nosepoke_back.scad]
2023-02-28 boards cables and updated 5-choice protocol
2023-03-02 Update boards_cables
2023-03-08 update some of the designs, simplify the work pipeline by calling modules, instead of rewriting them
    [backpanel.3mf, backpanel.scad, base_in_case_needed.scad, curved_wall.scad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]
2023-03-08 update nose poke wall so that it will protude inside cage
    [curved_wall2.scad, curved_wall2.stl]
2023-03-08 update wall after printing
    [curved_wall.scad, curved_wall2.3mf, curved_wall2.scad]
2023-03-14 update code and some 3d designs
    [curved_wall2.3mf, curved_wall2.scad]
2023-03-17 update curved walll design for two part printing
    [curved_wall2.3mf, curved_wall2.scad]
2023-03-29 update 3d designs
    [backpanel.3mf, backpanel.scad, curved_wall2.scad, curved_wall2_no_holes.3mf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]
2023-05-05 change backpanel and the size of the hole for the pellet dispenser shoot
    [backpanel.3mf, backpanel.scad, curved_wall2.scad, grid.scad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]
2023-05-05 update backpanel to cover the entire backwall
    [backpanel.3mf, backpanel.scad]
2023-05-12 update designs
    [backpanel.3mf, backpanel.scad, food_dispenser_base.FCStd, rotor.FCStd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]
2023-07-24 new board dedicated for leds and light transistors
    [beehive.kicad_pcb, new_board2.kicad_pcb, new_board2.kicad_sch]
2023-07-24 update new board
    [5csrtt_bom.ods, beehive.kicad_pcb, new_board2.kicad_pcb, new_board2.kicad_sch]
2023-07-24 more updates
    [beehive.kicad_pcb]
2023-07-24 pcb version 0.1
    [new_board2-B_Adhesive.gbr, new_board2-B_Courtyard.gbr, new_board2-B_Cu.gbr, new_board2-B_Fab.gbr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]
2023-07-24 update board
    [new_board2.kicad_pcb]
2023-08-04 add first version of new board
    [new_board2.kicad_pcb, new_board2.kicad_sch]
2023-10-24 update food dispenser
    [food_dispenser_base.FCStd, food_hopper_assembly-base_n_motor_holder.amf, food_hopper_assembly-motor_base.amf, food_hopper_assembly-rotor_final.amf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]
2023-10-24 create dedicated main board
    [main_pcb.kicad_pcb, main_pcb.kicad_sch]
2023-11-02 update base
    [base.FCStd]
2023-11-02 update gitgnore and cleanup 3d files
    [food_hopper_assembly-base_n_motor_holder.amf, food_hopper_assembly-motor_base.amf, food_hopper_assembly-rotor_final.amf, food_hopper_assembly.amf]
2023-11-03 update food hopper
    [base.FCStd, rotor.FCStd, rotor.stl]
2023-11-13 update printed parts
    [base.FCStd, base_test.stl, rotor.FCStd]
2023-11-18 clean up repo and make cap for food dispenser
    [all_parts-base.stl, all_parts-cap.stl, all_parts-chute_with_mount.stl, all_parts-motor_holder.stl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]
2023-11-18 clean up
    [base-base.stl, base-chute_with_mount.stl, base-motor_holder.stl]
2023-11-18 improve lid
    [all_parts-lid.stl, all_parts.FCStd]
2023-11-21 add backpanel
    [backpanel.stl]
2023-11-21 add missing stls
    [curved_wall2_noholes.stl, grid.stl, grid_with_support.stl]
2023-11-30 clean up repo
    [Unnamed1-Cut.amf, backpanel.3mf, backpanel.stl, base.stl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]
2023-11-30 update lid (non-critical)
    [all_parts-cap.stl, all_parts.FCStd]
2023-12-15 new rotor design
    Updated the rotor design to accurately fits the measurements of the dispenser lid.
    Moved the previous version (.fcstd, .stl) to archive folder
    [rotor.FCStd, rotor.stl, rotor_v3.FCStd, rotor_v3.stl]
2024-01-18 create code to test the servo and IR beams
    [mouse1_Phase4-8_07_04_2023-14_21_46.csv, mouse1_Phase4-8_07_04_2023-14_54_32.csv, mouse1_Phase4-8_07_04_2023-14_55_08.csv, mouse1_Phase4-8_07_04_2023-14_55_49.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]
2024-02-05 mount with chute new versions
    Uploaded FreeCad and STL files of new versions of pellet dispenser part (Mount with chute versions 2-6)
    [SG90 Servo.STEP, all_parts.FCStd, all_parts_chute_with_mount_v2.FCStd, all_parts_chute_with_mount_v3.FCStd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]
2024-09-11 Documentation and html site
    [28BYJ-48 5V Stepper Motor.stp, 5csrtt_bom.ods, Allparts.stl, Electronics_box_top.stl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]
2024-09-19 Documentation update
    [Curved_wall.stl, Ecase_Top.step, Electronics_box_top.stl, Electronics_top.stl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]
2024-09-19 reorganise location of files and fix small typo mistakes
    [28BYJ-48 5V Stepper Motor.stp, Allparts.stl, Curved_wall.stl, Electronics_top.stl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]
2024-09-23 Improved on documentation
    [Feed_tank.stl, Handle.stl, Motor_holder.stl, Rotor.stl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]
2024-09-30 link to read me png added
    [Handle.stl, Production_cost.xlsx, chute_with_mount.stl]
2025-02-11 add pellet dispenser as submodule, rename schematics to printed circuit board, fix typos
    [Feed_tank.stl, Handle.step, Handle.stl, Motor_holder.stl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]
2025-02-13 clean up code and move reward system from stepper to servo motor
2025-03-27 edited feeding wall and lid
    [Base_modified.stl, Feeding_wall.stl, Motor_holder_modified.stl]
2025-06-10 change pins for sensors and fix magazine training
2025-06-10 change variables names to something more explicit: 'buttons' are now sensors, etc
2025-06-27 one more pass at the pcb

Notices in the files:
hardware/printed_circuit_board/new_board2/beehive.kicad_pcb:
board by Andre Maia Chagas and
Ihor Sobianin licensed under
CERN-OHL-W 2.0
